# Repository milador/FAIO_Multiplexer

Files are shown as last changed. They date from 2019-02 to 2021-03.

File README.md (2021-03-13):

 # FAIO Multiplexer Switch 

FAIO Multiplexer is an open-source Assistive technology wing for Adafruit Feather boards which enables those with limited or no hand movement to use Adaptive switches as input to operate in multiple input modes.

<p align="center">
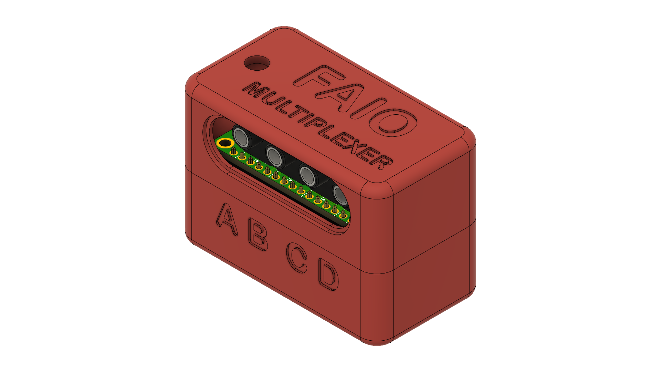
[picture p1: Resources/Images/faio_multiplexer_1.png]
FAIO Multiplexer 1

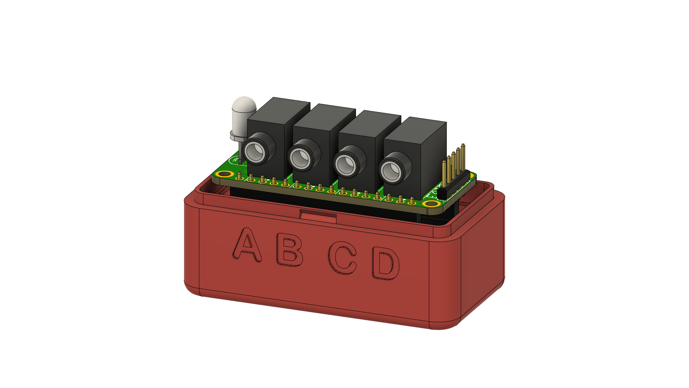
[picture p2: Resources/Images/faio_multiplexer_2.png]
FAIO Multiplexer 2

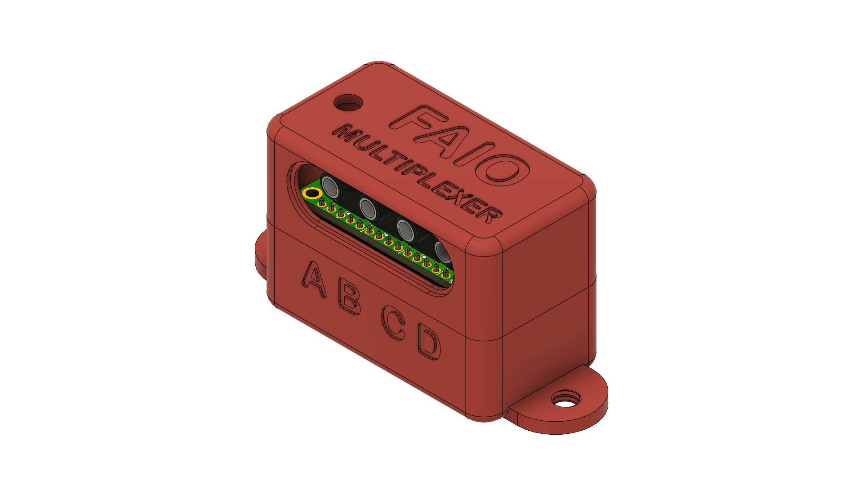
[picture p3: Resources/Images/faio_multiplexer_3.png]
FAIO Multiplexer 3

</p>

FAIO Multiplexer USB supports following switch modes:

* Switch Access Mode ( HID Keyboard ) : Teal Led
* Morse Keyboard Mode ( HID Keyboard ) : Purple Led
* Morse Mouse Mode ( HID Mouse ) : Pink Led
* Settings Mode : Orange Led

FAIO Multiplexer Joystick supports following switch modes:

* Mode 1 (Button 1,Button 2,Button 3,Button 4) : Teal Led
* Mode 2 (Button 5,Button 6,Button 7,Button 8) : Pink Led
* Settings Mode : Orange Led

How to change the mode?

You can change the mode by holding switch number 4 or D for 2 seconds.

Additional firmware to operate Xbox Adaptive Controller using switch module is available as well.

# Downloads 

These are all the files and documentation associated with the FAIO Multiplexer project.

 <table style="width:100%">
  <tr>
    <th>Resource</th>
    <th>Version</th>
    <th>Format</th>
    <th>Link</th>
  </tr>
    <tr>
    <td>FAIO Multiplexer All</td>
    <td>1.1</td>
    <td>ZIP</td>
    <td><a href="https://github.com/milador/FAIO_Multiplexer/archive/master.zip">FAIO_Multiplexer-master.zip</a></td>
  </tr>
  <tr>
    <td>FAIO_Multiplexer Assembly Manual</td>
    <td>Version 1.11</td>
    <td>PDF</td>
    <td><a href="https://github.com/milador/FAIO_Multiplexer/blob/master/Documentation/Build_Manuals/FAIO_Multiplexer_Instructions_Manual.pdf">FAIO_Multiplexer_Instructions_Manual.pdf</a></td>
  </tr>
   <tr>
    <td>FAIO_Multiplexer USB User Manual</td>
    <td>Version 1.1</td>
    <td>PDF</td>
    <td><a href="https://github.com/milador/FAIO_Multiplexer/blob/master/Documentation/User_Manuals/FAIO_Multiplexer_USB_User_Manual.pdf">FAIO_Multiplexer_USB_User_Manual.pdf</a></td>
  </tr>
    <tr>
    <td>FAIO_Multiplexer Joystick User Manual</td>
    <td>Version 1.1</td>
    <td>PDF</td>
    <td><a href="https://github.com/milador/FAIO_Multiplexer/blob/master/Documentation/User_Manuals/FAIO_Multiplexer_Joystick_User_Manual.pdf">FAIO_Multiplexer_Joystick_User_Manual.pdf</a></td>
  </tr>
  <tr>
    <td>FAIO_Multiplexer Switch BOM (csv)</td>
    <td>Jan 11, 2021</td>
    <td>CSV</td>
    <td><a href="https://github.com/milador/FAIO_Multiplexer/blob/master/Components/FAIO_Multiplexer_BOM.csv">FAIO_Multiplexer_BOM.csv</a></td>
  </tr>
  <tr>
    <td>FAIO_Multiplexer Switch BOM (HTML)</td>
    <td>March 12, 2021</td>
    <td>HTML</td>
    <td><a href="http://milador.ca/projects/faio_multiplexer/bom.html">bom.html</a></td>
  </tr>
  <tr>
    <td>FAIO_Multiplexer USB Switch Software</td>
    <td>1.0</td>
    <td>Ino</td>
    <td><a href="https://github.com/milador/FAIO-2/raw/master/Software/FAIO_Multiplexer_USB_Software/FAIO_Multiplexer_USB_Software.ino">FAIO_Multiplexer_USB_Software.ino</a></td>
  </tr>
  <tr>
    <td>FAIO_Multiplexer Joystick Switch Software</td>
    <td>1.0</td>
    <td>Ino</td>
    <td><a href="https://github.com/milador/FAIO-2/raw/master/Software/FAIO_Multiplexer_Joystick_Software/FAIO_Multiplexer_Joystick_Software.ino">FAIO_Multiplexer_Joystick_Software.ino</a></td>
  </tr>
  <tr>
    <td>FAIO_Multiplexer Switch Board Layout</td>
    <td>1.0</td>
    <td>BRD</td>
    <td><a href="https://raw.githubusercontent.com/milador/FAIO_Multiplexer/master/Hardware/PCB_design/FAIO_Multiplexer.brd">FAIO_Multiplexer.brd</a></td>
  </tr>
  <tr>
    <td>FAIO_Multiplexer Switch Board Schematic</td>
    <td>1.0</td>
    <td>SCH</td>
    <td><a href="https://raw.githubusercontent.com/milador/FAIO_Multiplexer/master/Hardware/PCB_design/FAIO_Multiplexer.sch">FAIO_Multiplexer.sch</a></td>
  </tr>
   <tr>
    <td>FAIO_Multiplexer Battery Holder enclosure</td>
    <td>1.1</td>
    <td>STL</td>
    <td><a href="https://github.com/milador/FAIO_Multiplexer/blob/master/Hardware/Housing_design/STL/FAIO_Multiplexer_Body_Battery_Holder.stl">FAIO_Multiplexer_Body_Battery_Holder.stl</a></td>
  </tr>
  <tr>
    <td>FAIO_Multiplexer Bottom enclosure</td>
    <td>1.1</td>
    <td>STL</td>
    <td><a href="https://github.com/milador/FAIO_Multiplexer/blob/master/Hardware/Housing_design/STL/FAIO_Multiplexer_Body_Bottom.stl">FAIO_Multiplexer_Body_Bottom.stl</a></td>
  </tr>
  <tr>
    <td>FAIO_Multiplexer Bottom enclosure with camera mount threaded screw hole</td>
    <td>1.1</td>
    <td>STL</td>
    <td><a href="https://github.com/milador/FAIO_Multiplexer/blob/master/Hardware/Housing_design/STL/FAIO_Multiplexer_Body_Bottom_With_Mount.stl">FAIO_Multiplexer_Body_Bottom_With_Mount.stl</a></td>
  </tr>
  <tr>
    <td>FAIO_Multiplexer Top enclosure</td>
    <td>1.1</td>
    <td>STL</td>
    <td><a href="https://github.com/milador/FAIO_Multiplexer/blob/master/Hardware/Housing_design/STL/FAIO_Multiplexer_Body_Top.stl">FAIO_Multiplexer_Body_Top.stl</a></td>
  </tr>
</table> 

# Usage

The FAIO Multiplexer switch interface can operate in 4 modes and switch D is used to switch between them.The RGB Led blinks 2 times to indicate the current mode.

<p align="center">
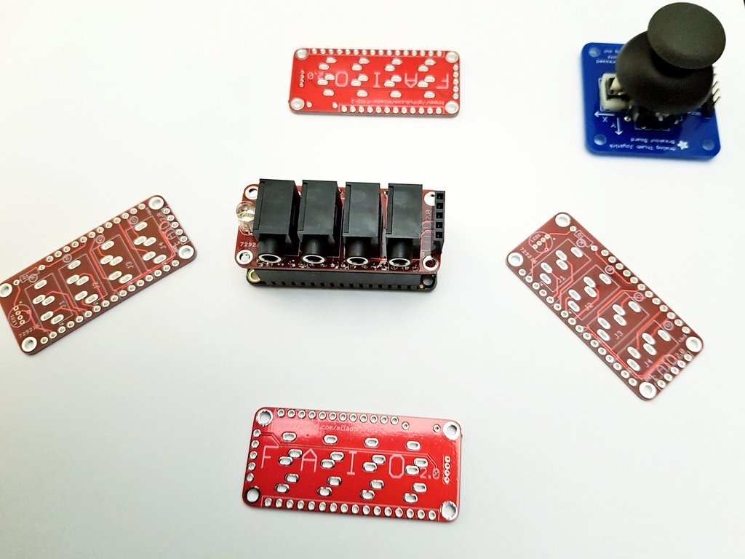
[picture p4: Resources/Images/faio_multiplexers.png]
FAIO Multiplexer boards

</p>

## USB or Bluetooth Switch mode

 <table style="width:100%">
  <tr>
    <th>Mode Number</th>
    <th>Mode</th>
    <th>Color</th>
  </tr>
    <tr>
    <td>1</td>
    <td>Keyboard Switch</td>
    <td>Teal</td>
  </tr>
  <tr>
    <td>2</td>
    <td>Morse Keyboard</td>
    <td>Purple</td>
  </tr>
  <tr>
    <td>3</td>
    <td>Morse Mouse</td>
    <td>Pink</td>
  </tr>
  <tr>
    <td>4</td>
    <td>Settings</td>
    <td>Orange</td>
  </tr>
</table> 

<p align="center">
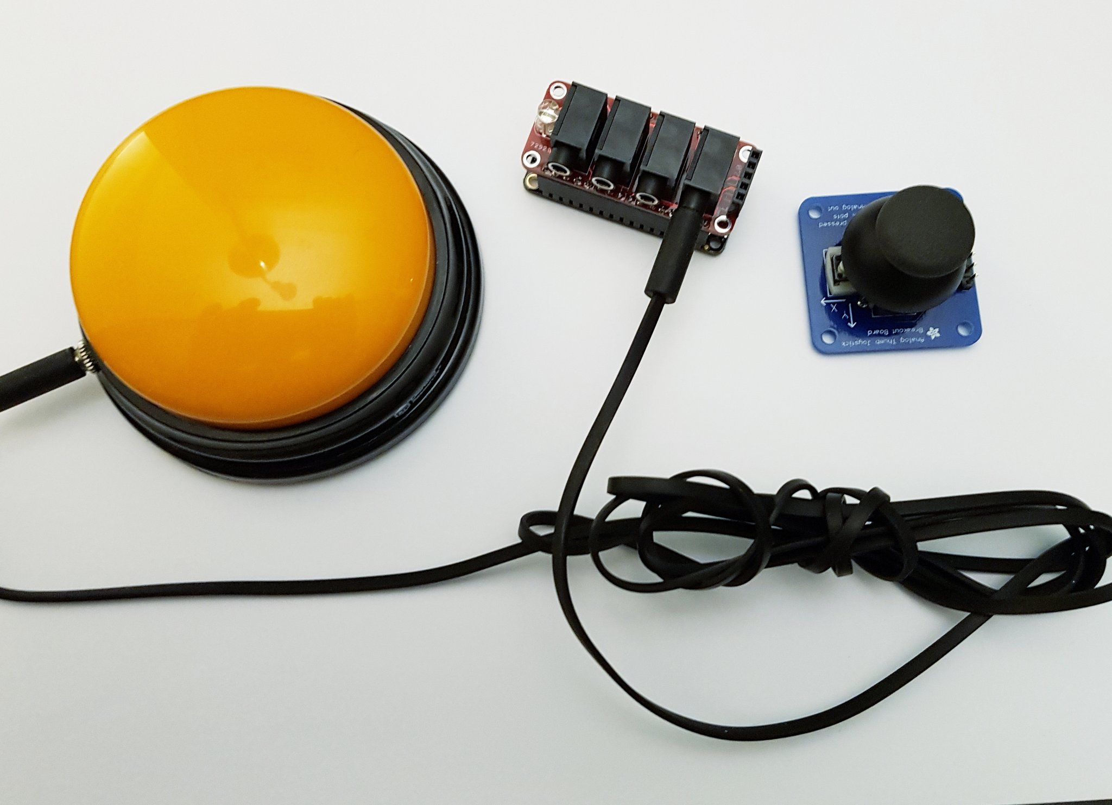
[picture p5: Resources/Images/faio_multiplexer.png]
FAIO Multiplexer board

</p>

## Joystick Switch mode

 <table style="width:100%">
  <tr>
    <th>Joystick Button Number (Mode 1,Mode 2)</th>
    <th>Xbox Button</th>
    <th>Color</th>
  </tr>
    <tr>
    <td>(1,5)</td>
    <td>X1</td>
    <td>Blue</td>
  </tr>
  <tr>
    <td>(2,6)</td>
    <td>X2</td>
    <td>Yellow</td>
  </tr>
  <tr>
    <td>(3,7)</td>
    <td>A</td>
    <td>Green</td>
  </tr>
  <tr>
    <td>(4,8)</td>
    <td>B</td>
    <td>Red</td>
  </tr>
</table> 

## Software Setup Instructions

  1. Install the required libraries 
  
  1.1. Install Neo Pixels : https://github.com/adafruit/Adafruit_NeoPixel

  1.2. Install EasyMorse if using USB or Bluetooth version : https://github.com/milador/EasyMorse
  
  1.3. Install StopWatch if using USB or Bluetooth version : https://github.com/RobTillaart/Arduino/tree/master/libraries/StopWatch
  
  1.4. Install FlashStorage if using Feather M0 Board : https://github.com/cmaglie/FlashStorage

  1.5. Install Joystick library: https://github.com/MHeironimus/ArduinoJoystickLibrary or https://github.com/gdsports/ArduinoJoystickLibrary/tree/samd_patch
  
  2. Download the firmware 
  
  2.1. USB Firmware : https://github.com/milador/FAIO_Multiplexer/raw/master/Software/FAIO_Multiplexer_USB_Software/FAIO_Multiplexer_USB_Software.ino

  2.2. Joystick Firmware : https://github.com/milador/FAIO_Multiplexer/raw/master/Software/FAIO_Multiplexer_Joystick_Software/FAIO_Multiplexer_Joystick_Software.ino
  
  2.3. Bluetooth Firmware (Coming up)
  
  3. Setup Arduino IDE for your feather board according to the instructions on Adafruit website
  
  4. Verify and upload firmware code to your Feather Board

# License

## Creative Commons Attribution-NonCommercial-ShareAlike (CC-BY-NC-SA)

Copyright (c) 2018 Milador

A creative commons license that bans commercial use and requires you to release any modified works under this license.

<p align="center">
CC-BY-NC-SA
</p>

<br />This work is licensed under a <a rel="license" href="http://creativecommons.org/licenses/by-nc-sa/3.0/">Creative Commons Attribution-NonCommercial-ShareAlike 3.0 Unported License</a>.

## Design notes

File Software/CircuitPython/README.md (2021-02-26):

# FAIO-Multiplexer CircuitPython software setup

  1. Download latest version of [CircuitPython for Feather M0 Express UF2](https://circuitpython.org/board/feather_m0_express/)
  2. Plug your Feather M0 Express into your computer using a known-good USB cable
  3. Double-click the small RST (reset) button, and you will see the NeoPixel RGB LED turn green
  4. You will see a new disk drive appear called FEATHERBOOT under Device and Drivers 
  5. Drag the adafruit_circuitpython_etc.uf2 file to FEATHERBOOT
  6. The red LED will flash. Then, the FEATHERBOOT drive will disappear and a new disk drive called CIRCUITPY will appear
  7. Replace the code.py under CIRCUITPY drive with FAIO Multiplexer USB [code.py](https://raw.githubusercontent.com/milador/FAIO_Multiplexer/main/Software/CircuitPython/FAIO_Multiplexer_USB_Software/code.py)
  8. Drag and drop required libraries under CIRCUITPY drive in lib folder. [Required libraries](https://github.com/milador/FAIO_Multiplexer/tree/main/Software/CircuitPython/FAIO_Multiplexer_USB_Software/lib)
  9. The led on Enabled-Controller-Mini should turn to teal color

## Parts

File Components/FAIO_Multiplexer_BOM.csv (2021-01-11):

Index | Quantity | Digikey Part Number | Manufacturer Part Number | Description | Unit Price (US) | Total Price (US) | Link
1 | 1 | 1528-1514-ND | 2771 | FEATHER 32U4 BASIC PROTO | 19.95 |  | https://www.digikey.com/product-detail/en/adafruit-industries-llc/2771/1528-1514-ND/
2 | 1 | 1568-1213-ND | COM-12986 | ADDRESS LED DISC SER RGB 5MM 5PC | 2.95 |  | https://www.digikey.com/products/en?keywords=COM-12986
3 | 1 | 1528-1560-ND | 2886 | FEATHER HEADER KIT FML | 0.95 |  | https://www.digikey.com/product-detail/en/adafruit-industries-llc/2886/1528-1560-ND/
4 | 1 | CF14JT470RCT-ND | CF14JT470R | RES 470 OHM 1/4W 5% AXIAL | 0.1 |  | https://www.digikey.com/product-detail/en/stackpole-electronics-inc/CF14JT470R/CF14JT470RCT-ND/1830342
5 | 4 | CP1-3535NG-ND | SJ1-3535NG | CONN JACK STEREO 3.5MM R/A | 1.25 |  | https://www.digikey.com/product-detail/en/cui-inc/SJ1-3535NG/CP1-3535NG-ND
6 | 4 | 36-4687-ND | 4687 | HEX NUT 0.197" NYLON M2.5 | 0.15 |  | https://www.digikey.com/en/products/detail/keystone-electronics/4687/4499296
7 | 4 | 36-29334-ND | 29334 | MACH SCREW PAN SLOTTED M2.5X0.45 | 0.22 |  | https://www.digikey.com/en/products/detail/keystone-electronics/29334/1532988
8 | 1 | 732-5318-ND | 61300511121 | CONN HEADER VERT 5POS 2.54MM | 0.25 |  | https://www.digikey.com/product-detail/en/wurth-electronics-inc/61300511121/732-5318-ND
9 | 1 | 1528-1858-ND | 2750 | BATTERY LITHIUM 3.7V 350MAH (Optional) | 6.95 |  | https://www.digikey.com/en/products/detail/adafruit-industries-llc/2750/6612470
 |  |  |  |  | Subtotal | 30.68

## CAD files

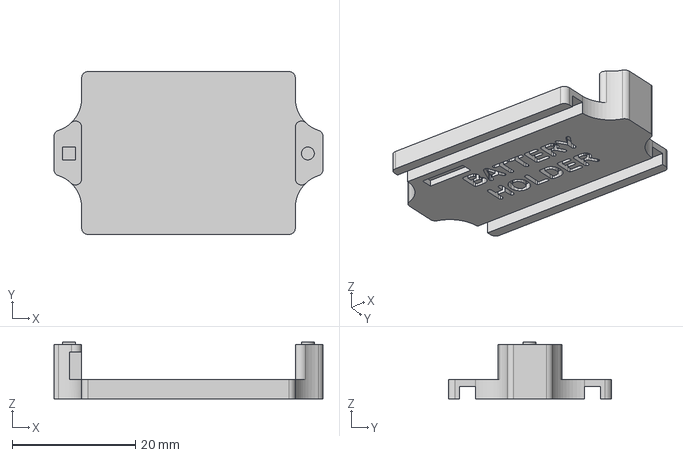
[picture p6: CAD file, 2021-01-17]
Hardware/Housing_design/STEP/FAIO_Multiplexer_Body_Battery_Holder.step
43.7 x 26.5 x 9.20 mm

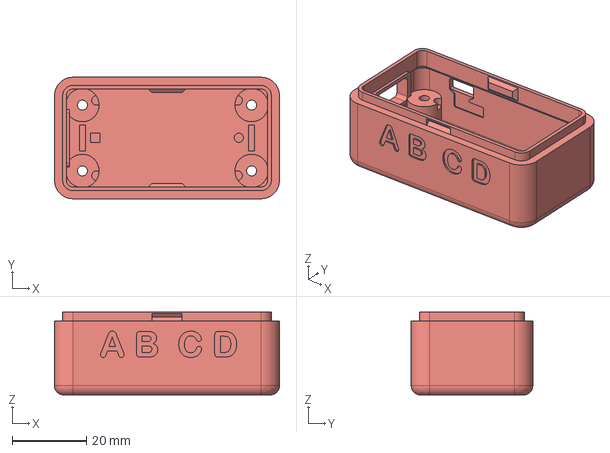
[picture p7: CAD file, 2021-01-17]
Hardware/Housing_design/STEP/FAIO_Multiplexer_Body_Bottom.step
60.8 x 32.9 x 22.4 mm

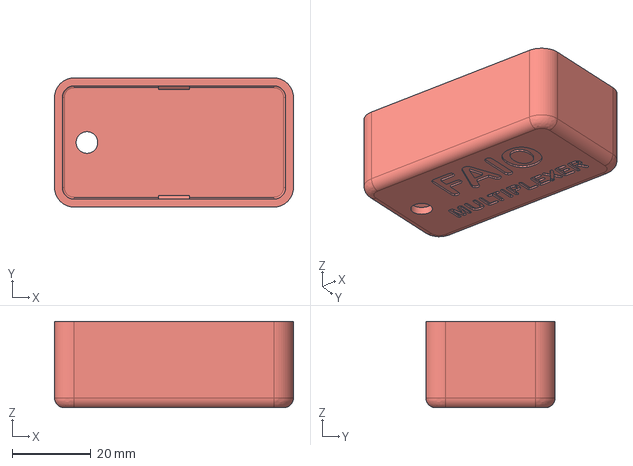
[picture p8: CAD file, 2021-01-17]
Hardware/Housing_design/STEP/FAIO_Multiplexer_Body_Top.step
60.8 x 32.9 x 22.0 mm

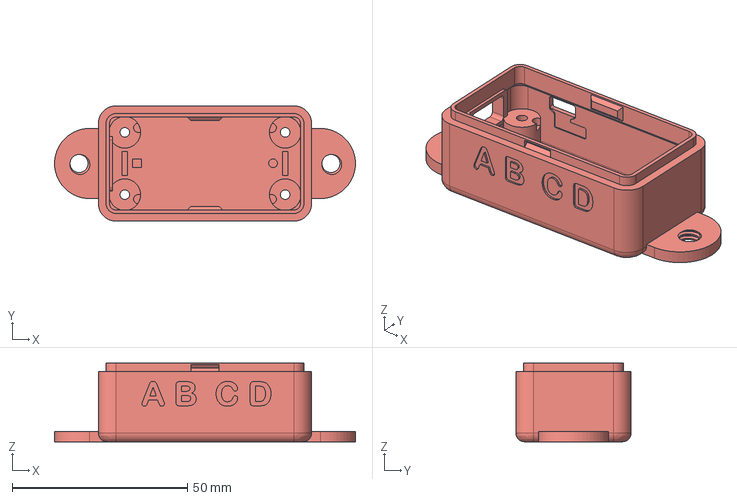
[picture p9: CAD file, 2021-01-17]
Hardware/Housing_design/STEP/FAIO_Multiplexer_Body_Bottom_With_Mount.step
85.8 x 32.9 x 22.4 mm

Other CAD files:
Hardware/Housing_design/STL/FAIO_Multiplexer_Body_Battery_Holder.stl
Hardware/Housing_design/STL/FAIO_Multiplexer_Body_Bottom.stl
Hardware/Housing_design/STL/FAIO_Multiplexer_Body_Bottom_With_Mount.stl
Hardware/Housing_design/STL/FAIO_Multiplexer_Body_Top.stl

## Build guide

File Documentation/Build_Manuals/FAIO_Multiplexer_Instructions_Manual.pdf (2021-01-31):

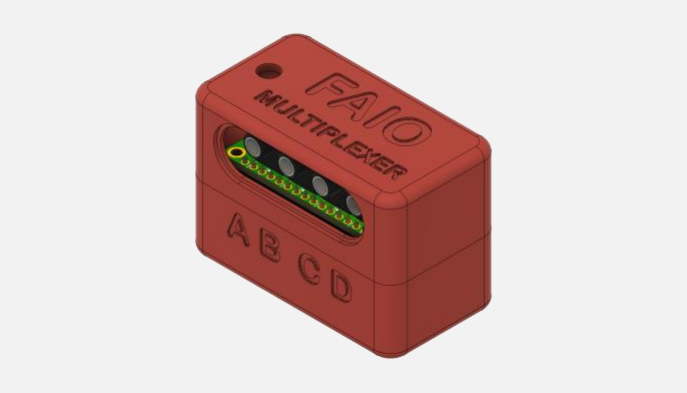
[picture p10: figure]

# FAIO MULTIPLEXER INSTRUCTIONS MANUAL (V1.11)

What if you could have a switch interface that would let you perform many actions using only 4 switches?

### Milad Hajihassan

https://github.com/milador/FAIO_Multiplexer

1

## Contents

Components List | 2
Software | 3
Installing Arduino Libraries | 3
USB Version | 3
Board Support Packages | 3
Required Software and libraries | 3
Uploading Software | 5
XAC Joystick Version | 6
Board Support Packages | 6
Required Software and libraries | 6
Uploading Software | 7
Wireless Version | 8
Board Support Packages | 8
Required Software and libraries | 8
Uploading Software | 10
Hardware Assembly | 11
Printed circuit Board design | 11
Enclosure design | 11
Assembly Instructions | 12

2

## Components List

1. ADAFRUIT FEATHER x 1
A. USB Version: ADAFRUIT FEATHER 32U4 BASIC PROTO or ADAFRUIT FEATHER M0 BASIC

PROTO

B. XAC Joystick Version: ADAFRUIT FEATHER 32U4 BASIC PROTO
C. Wireless Version: ADAFRUIT FEATHER 32U4 Bluefruit LE or ADAFRUIT FEATHER M0

Bluefruit LE

2. ADDRESS LED DISC SER RGB 5MM x 1
3. FEATHER HEADER KIT FML x 1
4. RES 470 OHM 1/4W 5% AXIAL x 1
5. CONN JACK STEREO 3.5MM R/A x 4
6. HEX NUT 0.197" NYLON M2.5 x 4
7. MACH SCREW PAN SLOTTED M2.5X0.45 x 4
8. CONN HEADER VERT 5POS 2.54MM (Optional: XAC Joystick version) x 1
9. BATTERY LITHIUM 3.7V 350MAH (Optional) x 1

The FAIO_Multiplexer_BOM or FAIO_Multiplexer bill of materials can also be downloaded from

GitHub repository under main directory.

https://github.com/milador/FAIO_Multiplexer/blob/master/Components/FAIO_Multiplexer_BOM.xlsx

3

## Software

The FAIO-Multiplexer software can be downloaded from the GitHub repository under software directory.

The FAIO_Multiplexer hardware can be used along different software as input device for multiple devices. The FAIO_Multiplexer software is offered in the following flavors:

1. USB Version: FAIO_Multiplexer_USB_Software (https://github.com/milador/FAIO_Multiplexer/tree/master/Software/FAIO_Multiplexer_USB_Software)
2. XAC Joystick Version: FAIO_Multiplexer_Joystick_Software (https://github.com/milador/FAIO_Multiplexer/tree/master/Software/FAIO_Multiplexer_Joystick_Software)
3. Wireless Version: FAIO_Multiplexer_Wireless_Software (https://github.com/milador/FAIO_Multiplexer_Wireless/tree/master/Software/FAIO_Multiplexer_Wireless_Software)

### Installing Arduino Libraries

The following instructions on how to install additional Arduino libraries helps you to get started with setting up Arduino IDE with required libraries and dependencies.

https://www.arduino.cc/en/guide/libraries

### USB Version

Board Support Packages
You can find the official instructions to install Board Support Packages on Adafruit website using following link:

https://learn.adafruit.com/adafruit-feather-m0-basic-proto/setup

https://learn.adafruit.com/adafruit-feather-32u4-basic-proto/arduino-ide-setup

Note: Please follow the instructions depending on your Adafruit Feather board model.

Alternatively, you can perform following instructions to install Board Support Packages:

1. Open and start the Arduino IDE.
2. Go to File > Preferences.

### 3. Add following link as a new line under Additional Board Manager URLs

- https://www.adafruit.com/package_adafruit_index.json

### 4. Restart the Arduino IDE 5. Open the Boards Manager option from the Tools > Board menu and install Adafruit SAMD

Boards by Adafruit or Adafruit SAMD Boards by Adafruit depending on your board.
6. Wait until the IDE finishes installing the cross-compiling toolchain and tools associated with Board Support Package. This may take few minutes.
7. That’s it! The installation of Board Support Packages is finished.

Required Software and libraries
The USB version of the software requires the following files and libraries:
- StopWatch library (https://github.com/RobTillaart/Stopwatch_RT)
- EasyMorse library (https://github.com/milador/EasyMorse)
- Adafruit_NeoPixel library (https://github.com/adafruit/Adafruit_NeoPixel)
- FlashStorage library (https://github.com/cmaglie/FlashStorage) (Optional: Only Feather M0 Board)

4

- FAIO_Multiplexer_USB_Software.ino (https://github.com/milador/FAIO_Multiplexer/blob/master/Software/FAIO_Multiplexer_USB_Software/FAIO_Multiplexer_USB_Software.ino)

StopWatch library helps to calculate the reaction time and timeout in the morse code interface.

EasyMorse library is used to provide morse code input interface by translating morse code into characters.

FAIO_Multiplexer is using Adafruit_NeoPixel library to provide visual feedback using RGB LED.

The Feather M0 Board does not come with EEPROM support and requires using FlashStorage library to handle saving variables and settings.

You can use the following instructions to download and install the required libraries:

1. Visit the StopWatch library (https://github.com/RobTillaart/Stopwatch_RT) github repository page.
2. Click on Code > Download Zip to download StopWatch library.

### 3. Extract Stopwatch_RT-master.zip file 4. Rename Stopwatch_RT-master folder to Stopwatch folder under Stopwatch_RT-master

subdirectory.
5. Copy or move Stopwatch folder to Arduino installation library subdirectory. As an example: This is found under C:\Program Files (x86)\Arduino\libraries in windows 10.
6. Visit the EasyMorse library (https://github.com/milador/EasyMorse) github repository page.
7. Click on Code > Download Zip to download EasyMorse library.

### 8. Extract EasyMorse.zip file

9. Rename EasyMorse-master folder to EasyMorse folder under EasyMorse-master subdirectory.
10. Copy or move EasyMorse folder to Arduino installation library subdirectory. As an example: This is found under C:\Program Files (x86)\Arduino\libraries in windows 10.
11. Visit the FlashStorage library (https://github.com/cmaglie/FlashStorage) github repository page.
12. Click on Code > Download Zip to download FlashStorage library.

### 13. Extract FlashStorage.zip file 14. Rename FlashStorage-master folder to FlashStorage folder under FlashStorage -master

subdirectory.
15. Copy or move FlashStorage folder to Arduino installation library subdirectory. As an example: This is found under C:\Program Files (x86)\Arduino\libraries in windows 10.
16. Visit the FAIO_Multiplexer_USB_Software.ino (https://github.com/milador/FAIO_Multiplexer/blob/master/Software/FAIO_Multiplexer_USB_Software/FAIO_Multiplexer_USB_Software.ino) raw source code file under FAIO_Multiplexer github repository page.

### 17. Right click on the source code or any place on this page and select Save Page As…

18. Select the directory you would like to save the software in your computer.
19. Change File name from FAIO_Multiplexer_USB_Software to FAIO_Multiplexer_USB_Software.ino
20. Change Save as type to All Files.
21. Click on Save button.
22. Open the directory you selected in step 18.

### 23. Double left click or open FAIO_Multiplexer_USB_Software file

5

### 24. Arduino IDE will ask your permission to create a new sketch folder named

FAIO_Multiplexer_USB_Software and move FAIO_Multiplexer_USB_Software.ino under this folder.
25. Click on the Ok button.
26. Arduino IDE should now open the FAIO_Multiplexer_USB_Software.ino file automatically.

Uploading Software
Note: Make sure all three files are included in your local copy of Software directory before uploading it to the Adafruit Feather board. The libraries can be installed in Arduino libraries.

You can go ahead and upload the downloaded. ino software to Adafruit Feather board using Arduino IDE once all the necessary libraries are installed.

1. Select the Board under Tools > Board > Adafruit Boards as Adafruit Feather 32u4 or under Tools > Board > Adafruit SAMD Boards as Adafruit Feather M0 based on your board.
2. Select the correct port number under Tools > Port which should say COM XX (Adafruit Feather 32u4) or COM XX (Adafruit Feather M0) based on your board

Note: It’s very important to make sure the correct Board and port number are selected as selecting the wrong board may result problems with bootloader of Adafruit Feather board.

3. Press the Verify button to make sure there is no problem with the software and libraries.
4. Press Upload button

Here you can see an example of my selected Board and port number.

Note: Your port number will not be the same

You can now go ahead and upload the software. Arduino IDE will show you a Done uploading message indicating the software is uploaded to your FAIO_Multiplexer.

The LED on the FAIO_Multiplexer main board blinks two times in green to indicate the start of initialization process has been started and it will blink again two times in green to indicate end of the initialization process.

You can also open the Serial Monitor in Arduino IDE on 115200 baud rate to read initialization information about the version of software.

6

### XAC Joystick Version

Board Support Packages
You can find the official instructions to install Board Support Packages on Adafruit website using following link:

https://learn.adafruit.com/adafruit-feather-32u4-basic-proto/arduino-ide-setup

Alternatively, you can perform following instructions to install Board Support Packages:

1. Open and start the Arduino IDE.
2. Go to File > Preferences.

### 3. Add following link as a new line under Additional Board Manager URLs

- https://www.adafruit.com/package_adafruit_index.json

### 4. Restart the Arduino IDE

5. Open the Boards Manager option from the Tools > Board menu and install Adafruit AVR Boards by Adafruit
6. Wait until the IDE finishes installing the cross-compiling toolchain and tools associated with Board Support Package. This may take few minutes.
7. That’s it! The installation of Board Support Packages is finished.

Required Software and libraries
The XAC Joystick version of the software requires the following files and libraries:
- StopWatch library (https://github.com/RobTillaart/Stopwatch_RT)
- Joystick library (https://github.com/MHeironimus/ArduinoJoystickLibrary)
- Adafruit_NeoPixel library (https://github.com/adafruit/Adafruit_NeoPixel)
- FAIO_Multiplexer_Joystick_Software.ino (https://github.com/milador/FAIO_Multiplexer/blob/master/Software/FAIO_Multiplexer_Joystick_Software/FAIO_Multiplexer_Joystick_Software.ino)

The joystick library is used to turn FAIO_Multiplexer into a joystick USB HID device which can be supported by Xbox adaptive controller.

FAIO_Multiplexer is using Adafruit_NeoPixel library to provide visual feedback using RGB LED.

You can use the following instructions to download and install the required libraries:

1. Visit the StopWatch library (https://github.com/RobTillaart/Stopwatch_RT) github repository page.
2. Click on Code > Download Zip to download StopWatch library.

### 3. Extract Stopwatch_RT-master.zip file 4. Rename Stopwatch_RT-master folder to Stopwatch folder under Stopwatch_RT-master

subdirectory.
5. Copy or move Stopwatch folder to Arduino installation library subdirectory. As an example: This is found under C:\Program Files (x86)\Arduino\libraries in windows 10.
6. Visit the Joystick library (https://github.com/MHeironimus/ArduinoJoystickLibrary) github repository page.

7

7. Click on Code > Download Zip to download ArduinoJoystickLibrary library.

### 8. Extract ArduinoJoystickLibrary.zip file

9. Copy or move Joystick folder under ArduinoJoystickLibrary-master subdirectory to Arduino installation library subdirectory. As an example: This is found under C:\Program Files (x86)\Arduino\libraries in windows 10.
10. Visit the FAIO_Multiplexer_Joystick_Software.ino (https://github.com/milador/FAIO_Multiplexer/blob/master/Software/FAIO_Multiplexer_Joystick_Software/FAIO_Multiplexer_Joystick_Software.ino) raw source code file under FAIO_Multiplexer github repository page.

### 11. Right click on the source code or any place on this page and select Save Page As…

12. Select the directory you would like to save the software in your computer.

### 13. Change File name from FAIO_Multiplexer_Joystick_Software to

FAIO_Multiplexer_Joystick_Software.ino
14. Change Save as type to All Files.
15. Click on Save button.
16. Open the directory you selected in step 12.

### 17. Double left click or open FAIO_Multiplexer_Joystick_Software file 18. Arduino IDE will ask your permission to create a new sketch folder named

FAIO_Multiplexer_Joystick_Software and move FAIO_Multiplexer_Joystick_Software.ino under this folder.
19. Click on the Ok button.
20. Arduino IDE should now open the FAIO_Multiplexer_Joystick_Software.ino file automatically.

Uploading Software
Note: Make sure all three files are included in your local copy of Software directory before uploading it to the Adafruit Feather board. The libraries can be installed in Arduino libraries.

You can go ahead and upload the downloaded. ino software to Adafruit Feather board using Arduino IDE once all the necessary libraries are installed.

### 1. Select the Board under Tools > Board > Adafruit Boards as Adafruit Feather 32u4

2. Select the correct port number under Tools > Port which should say COM XX (Adafruit Feather 32u4)

Note: It’s very important to make sure the correct Board and port number are selected as selecting the wrong board may result problems with bootloader of Adafruit Feather board.

3. Press the Verify button to make sure there is no problem with the software and libraries.

### 4. Press Upload button

Here you can see an example of my selected Board and port number.

Note: Your port number will not be the same

You can now go ahead and upload the software. Arduino IDE will show you a Done uploading message indicating the software is uploaded to your FAIO_Multiplexer.

8

The LED on the FAIO_Multiplexer main board blinks two times in green to indicate the start of initialization process has been started and it will blink again two times in green to indicate end of the initialization process.

You can also open the Serial Monitor in Arduino IDE on 115200 baud rate to read initialization information about the version of software.

### Wireless Version

Board Support Packages
You can find the official instructions to install Board Support Packages on Adafruit website using following links:

https://learn.adafruit.com/adafruit-feather-m0-bluefruit-le/setup

https://learn.adafruit.com/adafruit-feather-32u4-bluefruit-le//setup

Note: Please follow the instructions depending on your Adafruit Feather board model.

The wireless version of the FAIO_Multiplexer is using nRF51 Bluetooth chip to communicate with host devices. Bluetooth communication might seem complicated but Adafruit has made the bluetooth communication process less challenging by providing Adafruit nRF51 BLE Library which you can download from Adafruit and import it to your locally installed Arduino directory under libraries directory.

https://github.com/adafruit/Adafruit_BluefruitLE_nRF51

The instructions on how to install Adafruit nRF51 BLE Library can be found in following link:

https://learn.adafruit.com/adafruit-feather-32u4-bluefruit-le/installing-ble-library

Alternatively, you can perform following instructions to install Board Support Packages:

1. Open and start the Arduino IDE.
2. Go to File > Preferences.

### 3. Add following link as a new line under Additional Board Manager URLs

- https://www.adafruit.com/package_adafruit_index.json

### 4. Restart the Arduino IDE 5. Open the Boards Manager option from the Tools > Board menu and install Adafruit SAMD

Boards by Adafruit or Adafruit SAMD Boards by Adafruit depending on your board.
6. Wait until the IDE finishes installing the cross-compiling toolchain and tools associated with Board Support Package. This may take few minutes.
7. That’s it! The installation of Board Support Packages is finished.

Required Software and libraries
The wireless version of the software requires the following files and libraries:
- StopWatch library (https://github.com/RobTillaart/Stopwatch_RT)
- EasyMorseBlue library (https://github.com/milador/EasyMorseBlue)
- Adafruit_NeoPixel library (https://github.com/adafruit/Adafruit_NeoPixel)

9

- FlashStorage library (https://github.com/cmaglie/FlashStorage) (Optional: Only Feather M0 Board)
- Bluefruit Arduino Library (https://learn.adafruit.com/adafruit-feather-32u4-bluefruit-le/installing-ble-library)
- FAIO_Multiplexer_Wireless_Software.ino (https://github.com/milador/FAIO_Multiplexer_Wireless/blob/master/Software/FAIO_Multiplexer_Wireless_Software/FAIO_Multiplexer_Wireless_Software.inoare.ino)

StopWatch library helps to calculate the reaction time and timeout in the morse code interface.

The EasyMorseBlue library is the Bluetooth version of EasyMorse library which is used to enable the end user to use morse code or a sequence of dots and dashes as input method.

FAIO_Multiplexer is using Adafruit_NeoPixel library to provide visual feedback using RGB LED.

1. Visit the StopWatch library (https://github.com/RobTillaart/Stopwatch_RT) github repository page.
2. Click on Code > Download Zip to download StopWatch library.

### 3. Extract Stopwatch_RT-master.zip file 4. Rename Stopwatch_RT-master folder to Stopwatch folder under Stopwatch_RT-master

subdirectory.
5. Copy or move Stopwatch folder to Arduino installation library subdirectory. As an example: This is found under C:\Program Files (x86)\Arduino\libraries in windows 10.
6. Visit the EasyMorseBlue library (https://github.com/milador/EasyMorseBlue) github repository page.
7. Click on Code > Download Zip to download EasyMorseBlue library.

### 8. Extract EasyMorse.zip file 9. Rename EasyMorseBlue-master folder to EasyMorseBlue folder under EasyMorseBlue-master

subdirectory.
10. Copy or move EasyMorseBlue folder to Arduino installation library subdirectory. As an example: This is found under C:\Program Files (x86)\Arduino\libraries in windows 10.
11. Visit the FlashStorage library (https://github.com/cmaglie/FlashStorage) github repository page.
12. Click on Code > Download Zip to download FlashStorage library.

### 13. Extract FlashStorage.zip file 14. Rename FlashStorage-master folder to FlashStorage folder under FlashStorage -master

subdirectory.
15. Copy or move FlashStorage folder to Arduino installation library subdirectory. As an example: This is found under C:\Program Files (x86)\Arduino\libraries in windows 10.

### 16. Click on Sketch > Include Library > Manage Libraries…

17. Search for the Adafruit BluefruitLE nRF51 library and install it.
18. Visit the FAIO_Multiplexer_Wireless_Software.ino (https://github.com/milador/FAIO_Multiplexer_Wireless/blob/master/Software/FAIO_Multiplexer_Wireless_Software/FAIO_Multiplexer_Wireless_Software.inoare.ino) raw source code file under FAIO-Multiplexer github repository page.

### 19. Right click on the source code or any place on this page and select Save Page As…

20. Select the directory you would like to save the software in your computer.

### 21. Change File name from FAIO_Multiplexer_Wireless_Software to

FAIO_Multiplexer_Wireless_Software.ino
22. Change Save as type to All Files.
23. Click on Save button.
24. Open the directory you selected in step 20.

### 25. Double left click or open FAIO_Multiplexer_Wireless_Software file

10

### 26. Arduino IDE will ask your permission to create a new sketch folder named

FAIO_Multiplexer_Wireless_Software and move FAIO_Multiplexer_Wireless_Software.ino under this folder.
27. Click on the Ok button.
28. Arduino IDE should now open the FAIO_Multiplexer_Wireless_Software.ino file automatically.

Uploading Software
Note: Make sure all three files are included in your local copy of Software directory before uploading it to the Adafruit Feather board. The libraries can be installed in Arduino libraries.

You can go ahead and upload the downloaded. ino software to Adafruit Feather board using Arduino IDE once all the necessary libraries are installed.

1. Select the Board under Tools > Board > Adafruit Boards as Adafruit Feather 32u4 or under Tools > Board > Adafruit SAMD Boards as Adafruit Feather M0 based on your board.
2. Select the correct port number under Tools > Port which should say COM XX (Adafruit Feather 32u4) or COM XX (Adafruit Feather M0) based on your board

Note: It’s very important to make sure the correct Board and port number are selected as selecting the wrong board may result problems with bootloader of Adafruit Feather board.

1. Press the Verify button to make sure there is no problem with the software and libraries.

### 2. Press Upload button

You can now go ahead and upload the software. Arduino IDE will show you a Done Uploading message indicating the software is uploaded to your FAIO_Multiplexer.

The LED on the FAIO_Multiplexer main board blinks two times in teal to indicate the start of initialization process has been started and it will blink again two times in green to indicate end of the initialization process.

You can also open the Serial Monitor in Arduino IDE on 115200 baud-rate to read initialization information about the version of software.

11

## Hardware Assembly

### Printed circuit Board design

The printed circuit boards (PCB) can be downloaded from GitHub repository under Hardware directory.

https://github.com/milador/FAIO_Multiplexer/tree/master/Hardware/PCB_design

### Enclosure design

The enclosure/housing files in STL format can be downloaded from GitHub repository under Hardware directory.

https://github.com/milador/FAIO_Multiplexer/tree/master/Hardware/Housing_design

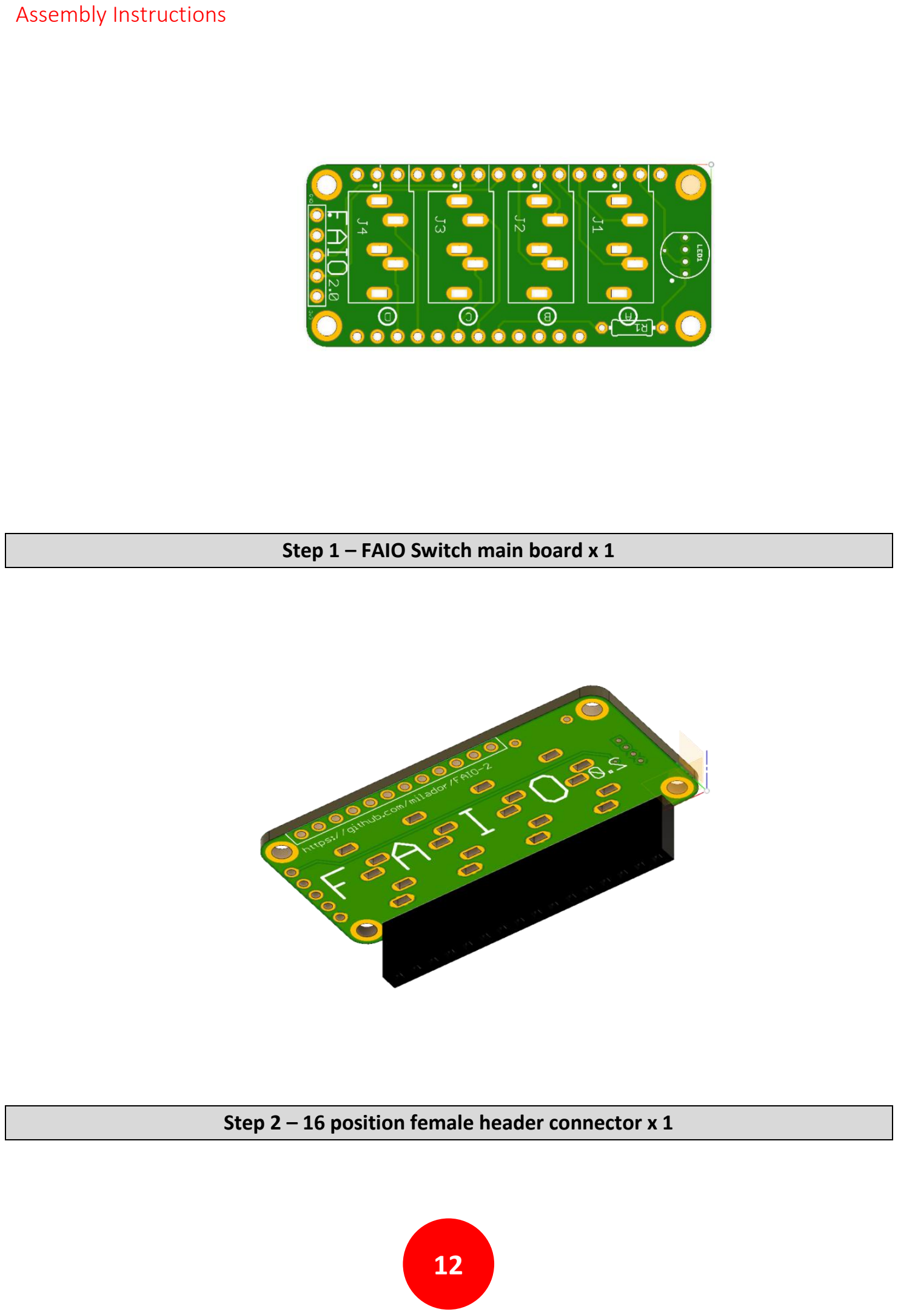
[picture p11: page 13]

12

### Assembly Instructions

Step 1 – FAIO Switch main board x 1
Step 2 – 16 position female header connector x 1

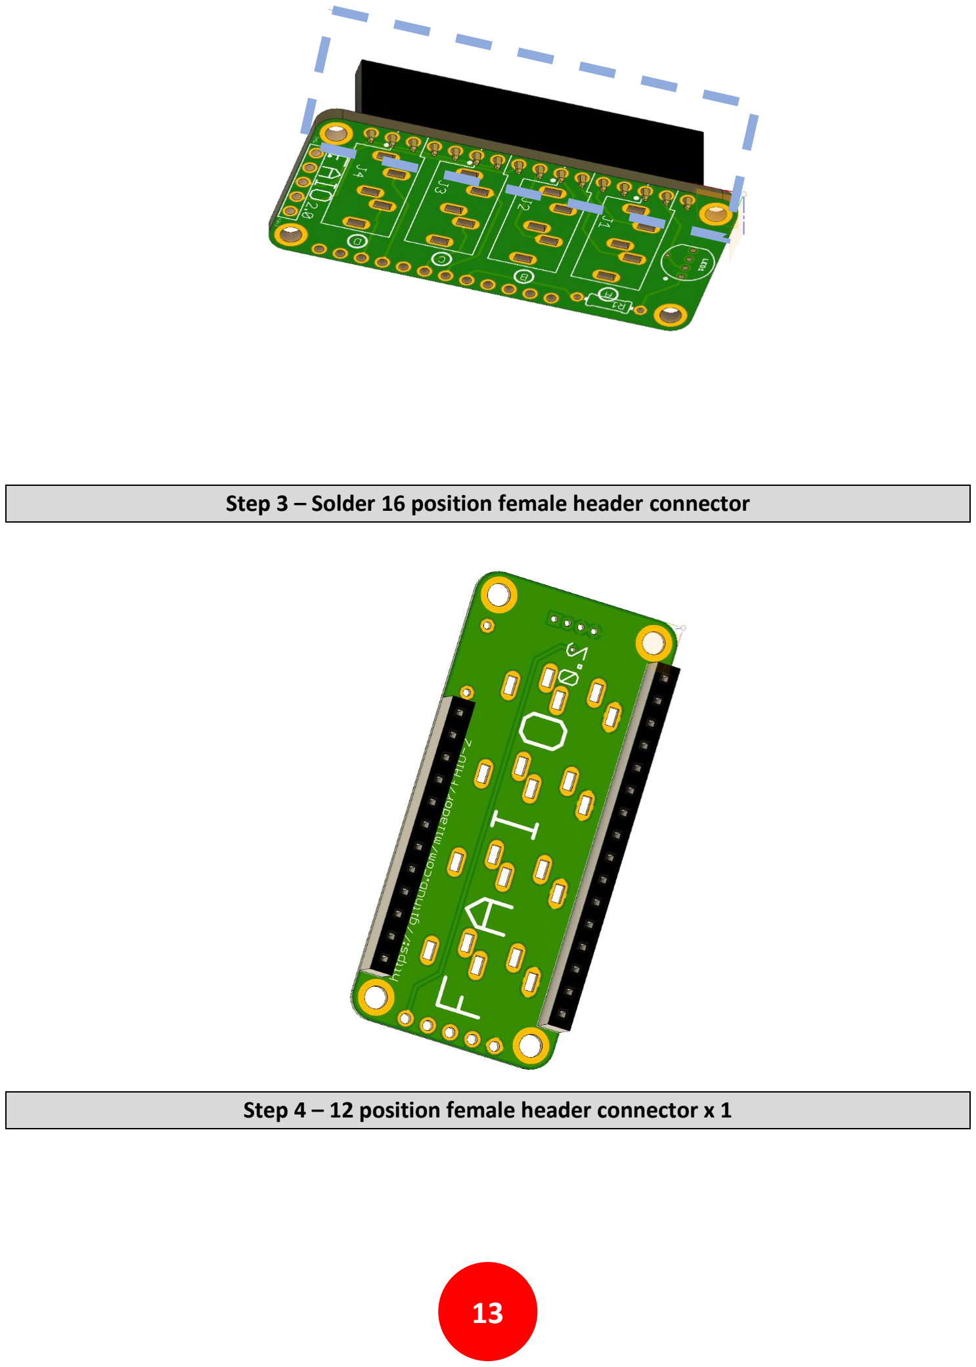
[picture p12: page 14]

13

Step 3 – Solder 16 position female header connector
Step 4 – 12 position female header connector x 1

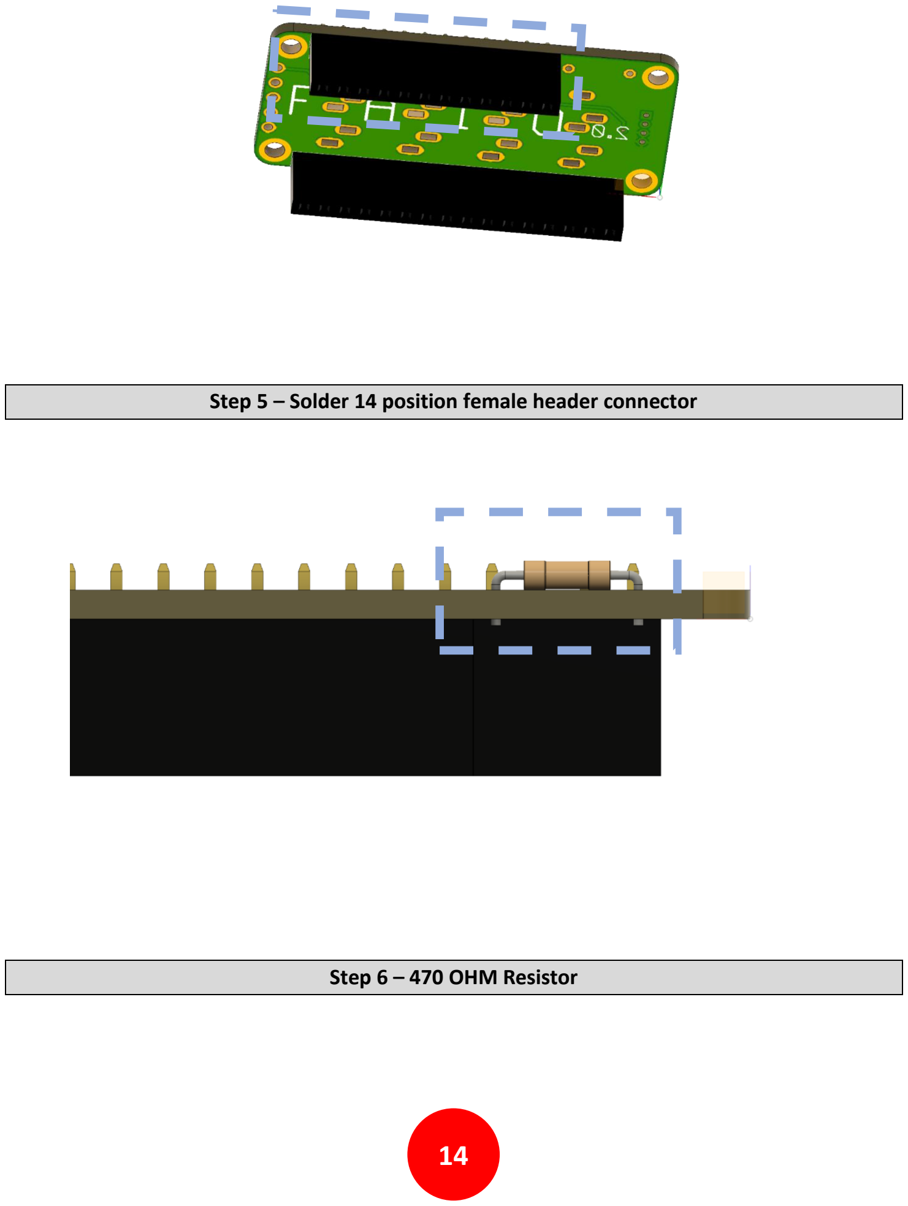
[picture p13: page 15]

14

Step 5 – Solder 14 position female header connector
Step 6 – 470 OHM Resistor

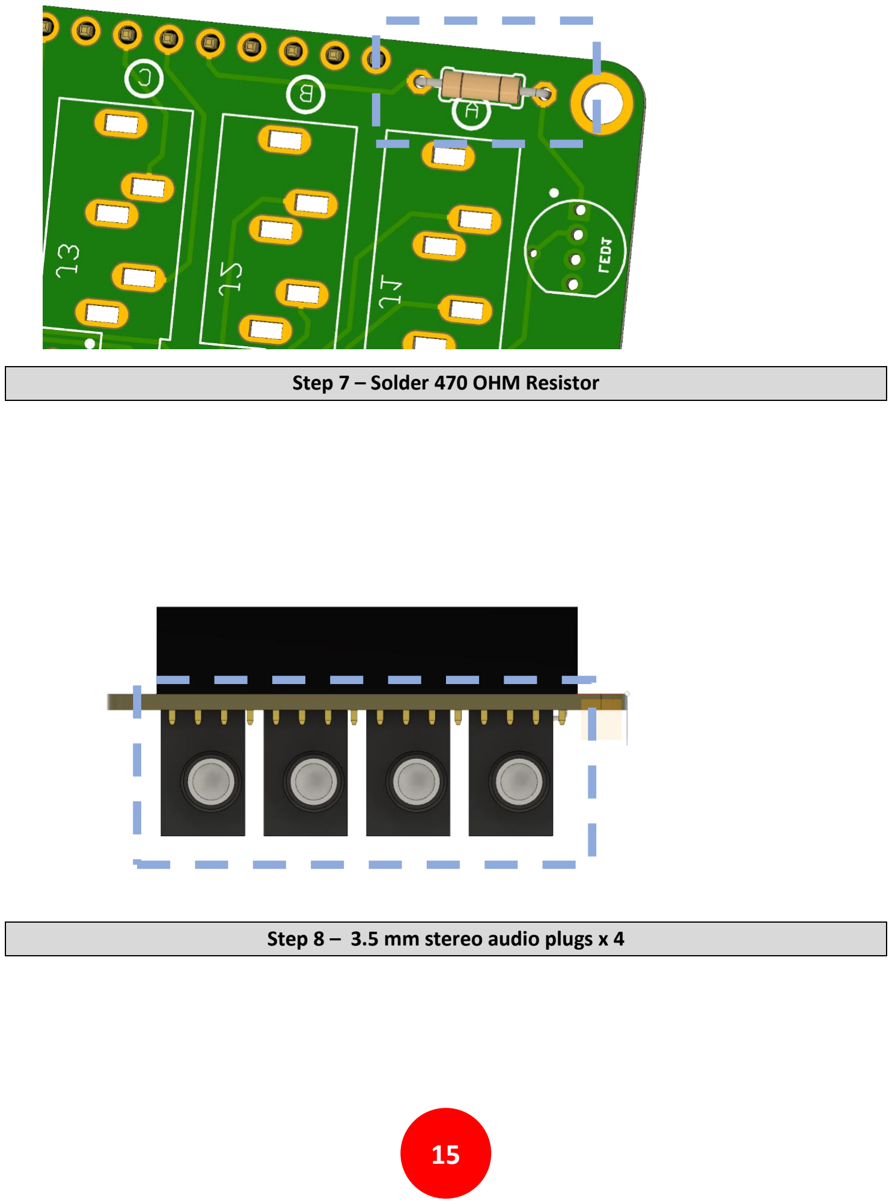
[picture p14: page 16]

15

Step 7 – Solder 470 OHM Resistor
Step 8 – 3.5 mm stereo audio plugs x 4

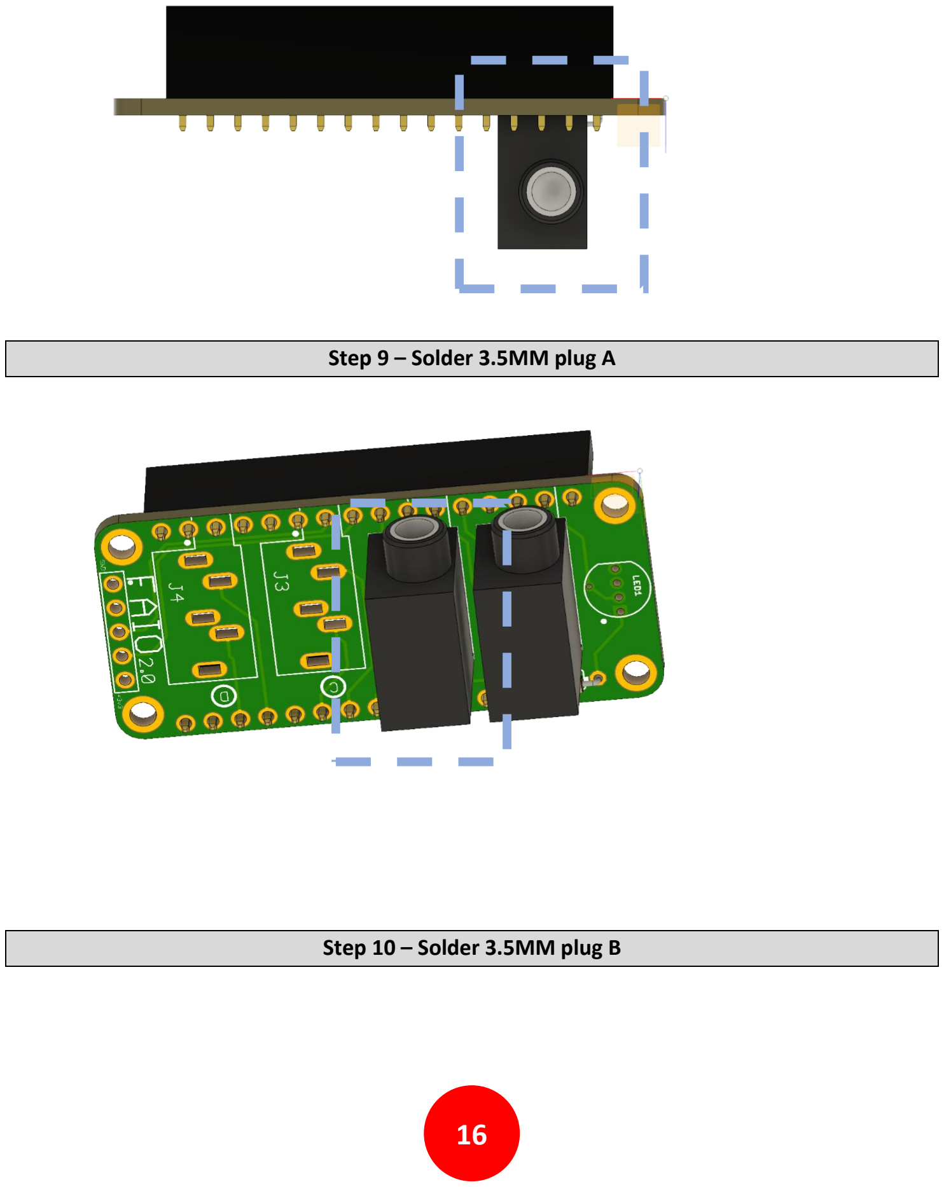
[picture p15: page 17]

16

Step 9 – Solder 3.5MM plug A
Step 10 – Solder 3.5MM plug B

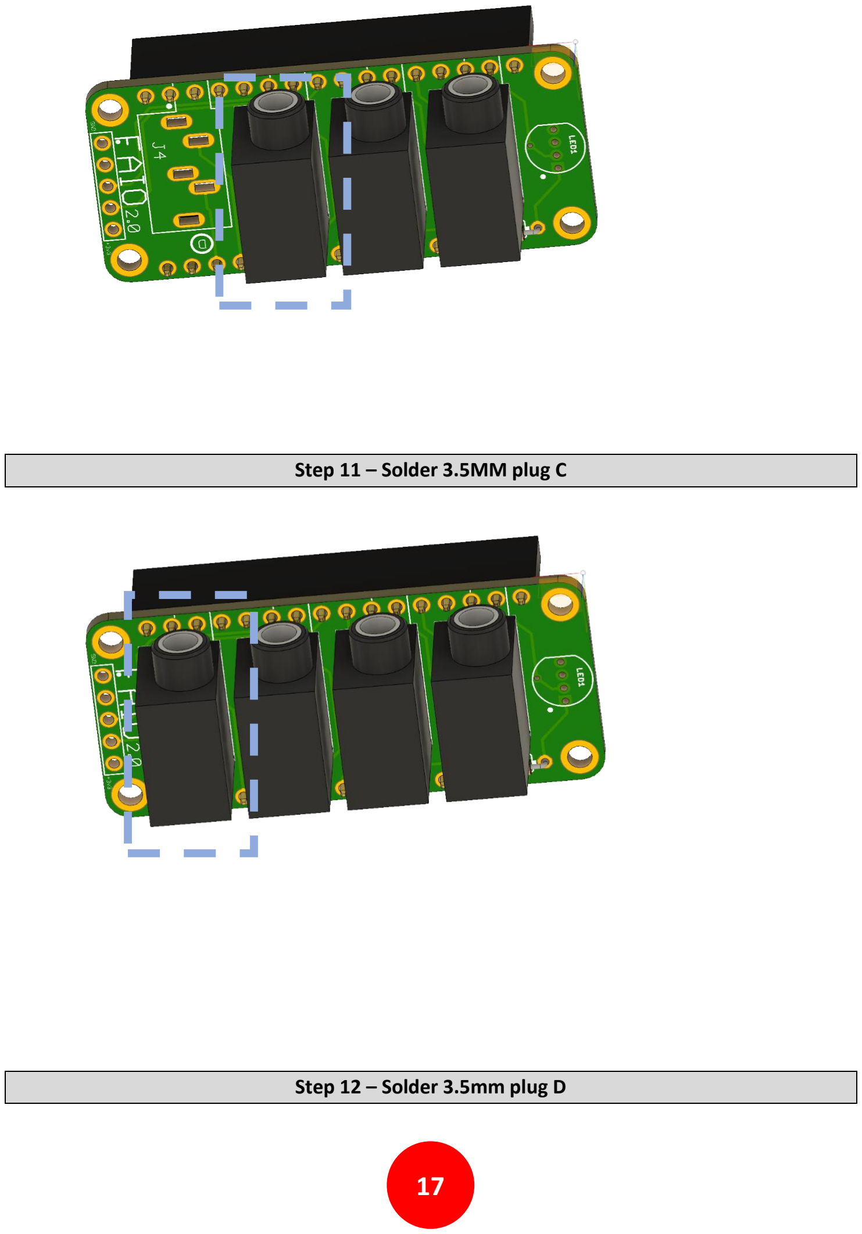
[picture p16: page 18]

17

Step 11 – Solder 3.5MM plug C
Step 12 – Solder 3.5mm plug D

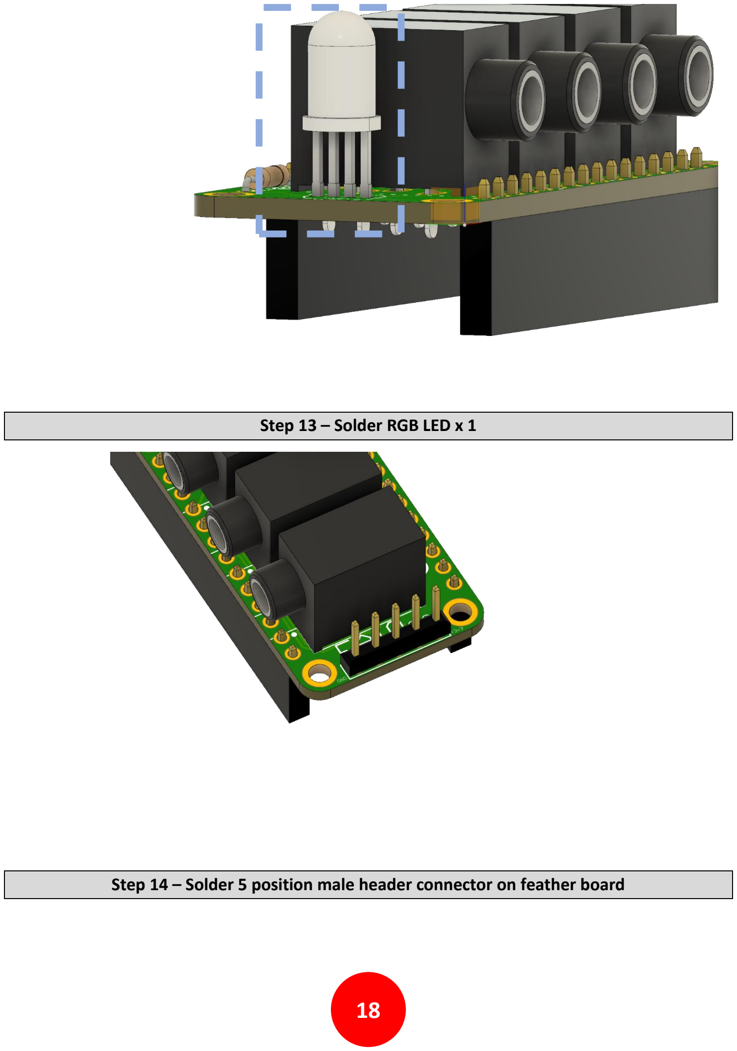
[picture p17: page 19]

18

Step 13 – Solder RGB LED x 1
Step 14 – Solder 5 position male header connector on feather board

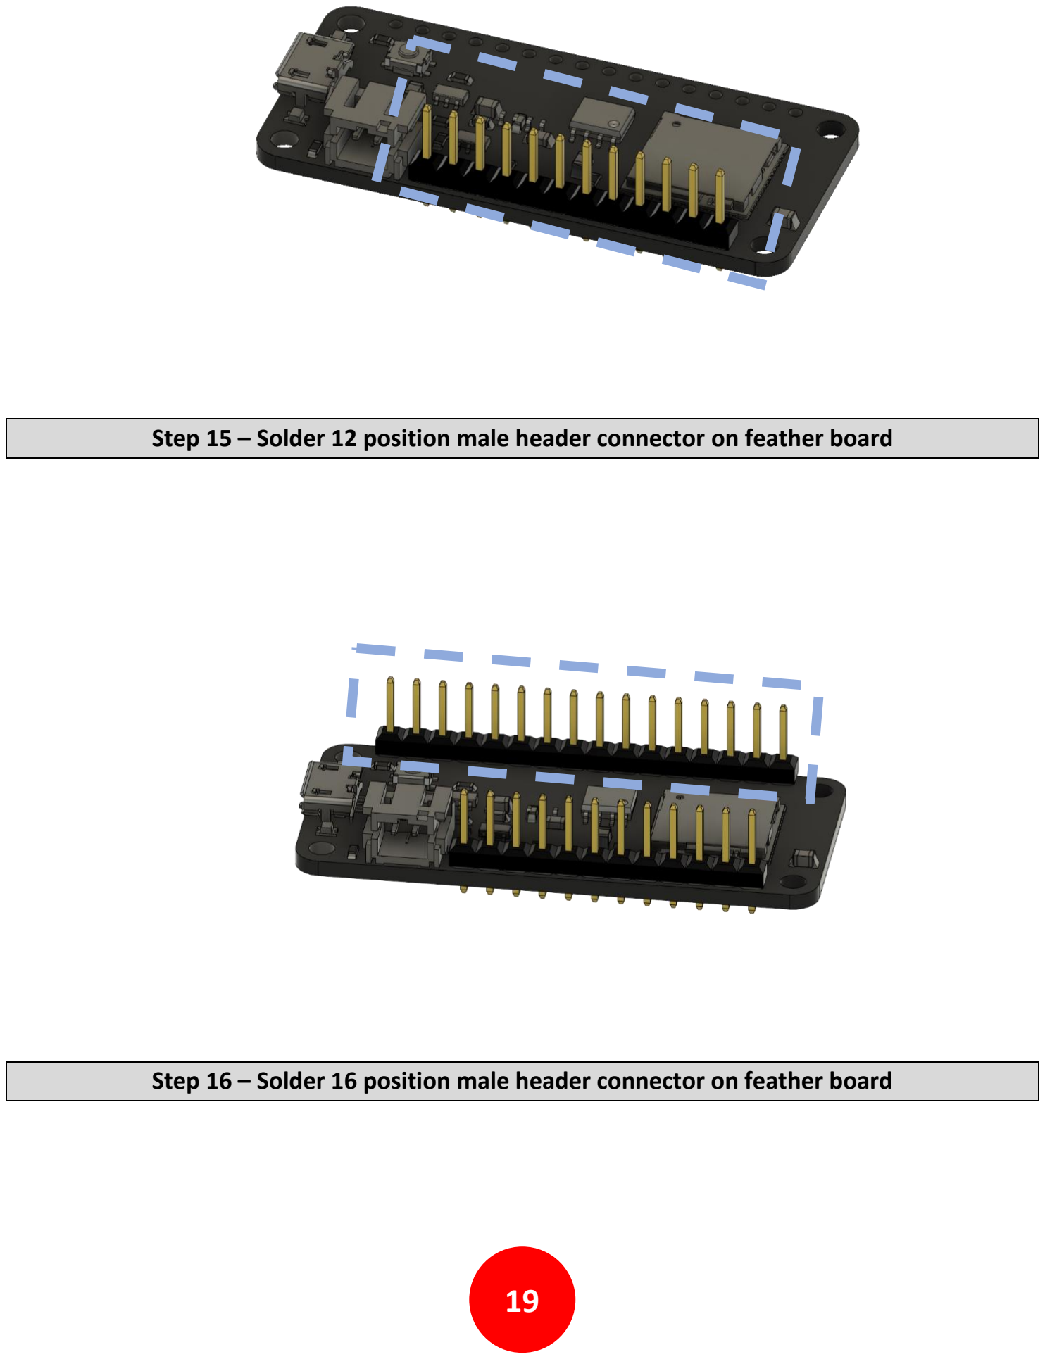
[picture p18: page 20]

19

Step 15 – Solder 12 position male header connector on feather board
Step 16 – Solder 16 position male header connector on feather board

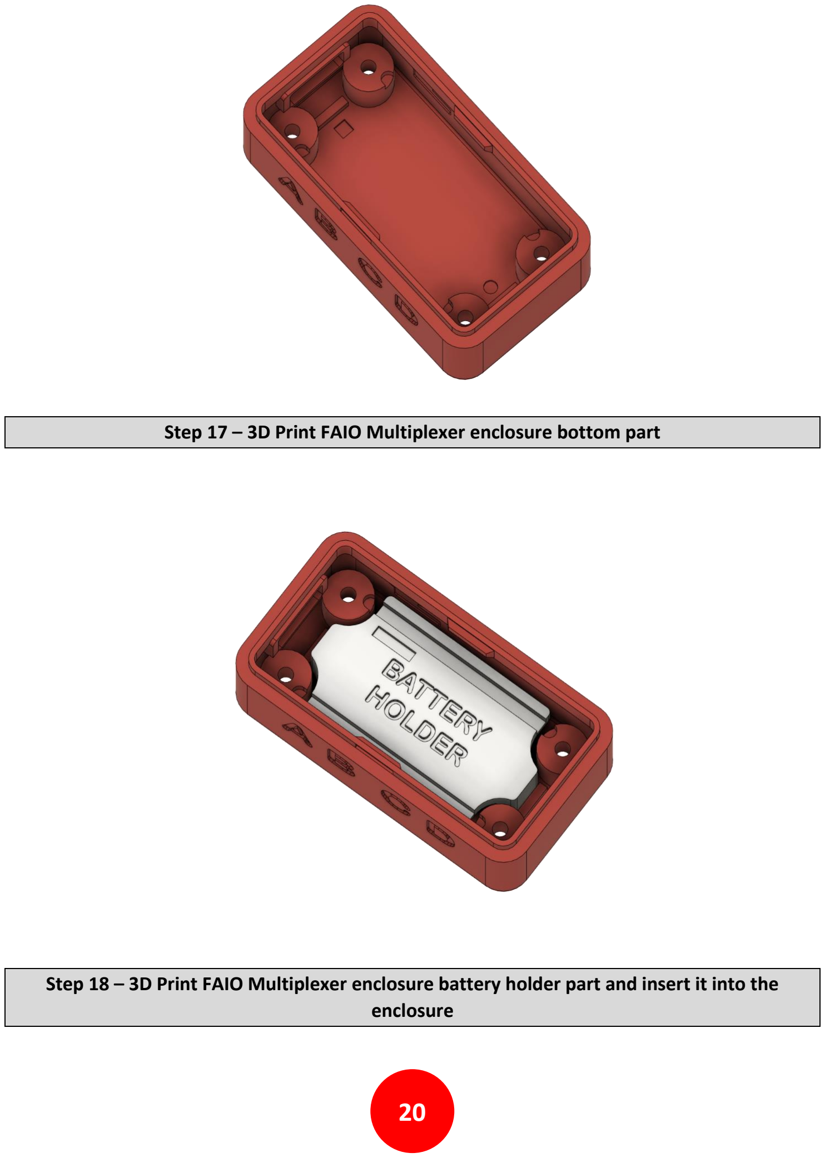
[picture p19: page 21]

20

Step 17 – 3D Print FAIO Multiplexer enclosure bottom part
Step 18 – 3D Print FAIO Multiplexer enclosure battery holder part and insert it into the enclosure

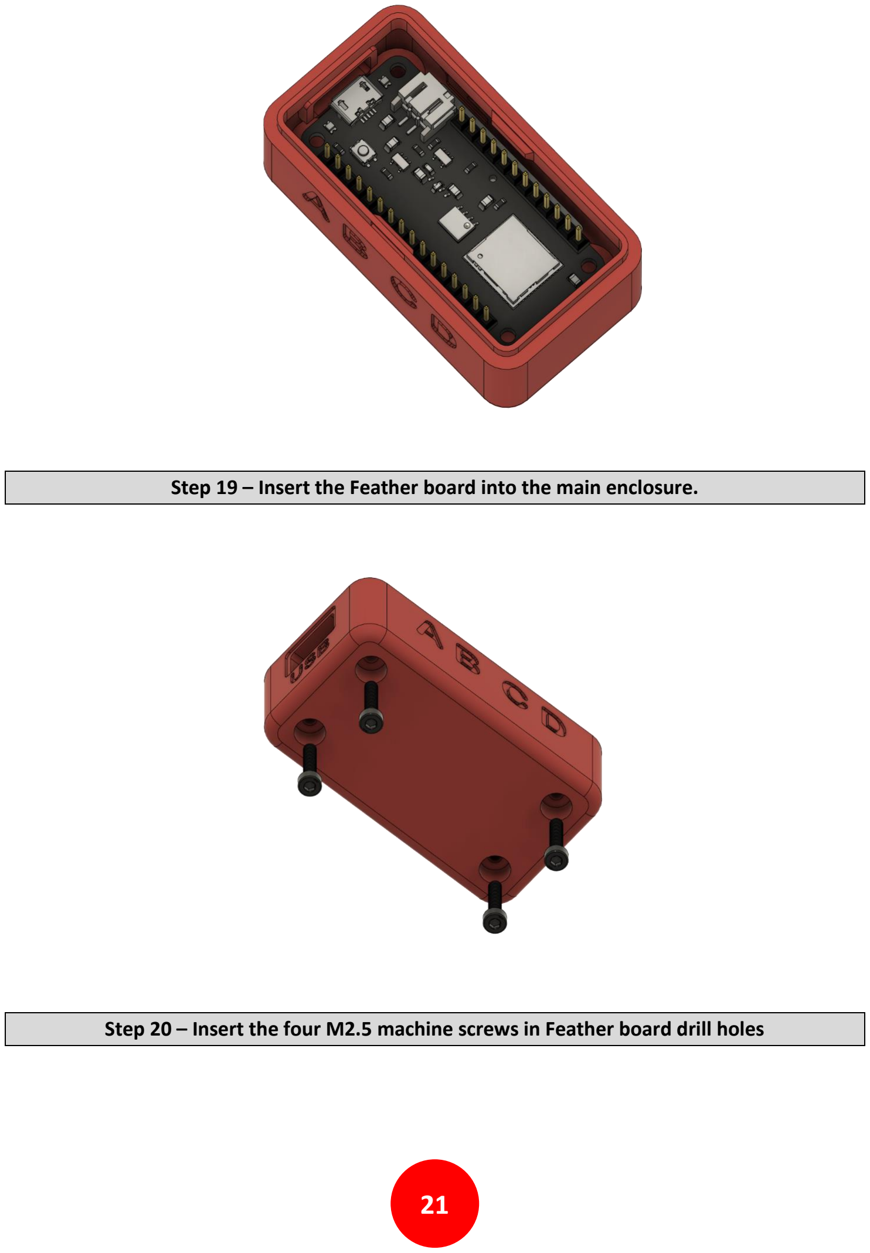
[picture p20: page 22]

21

Step 19 – Insert the Feather board into the main enclosure.
Step 20 – Insert the four M2.5 machine screws in Feather board drill holes

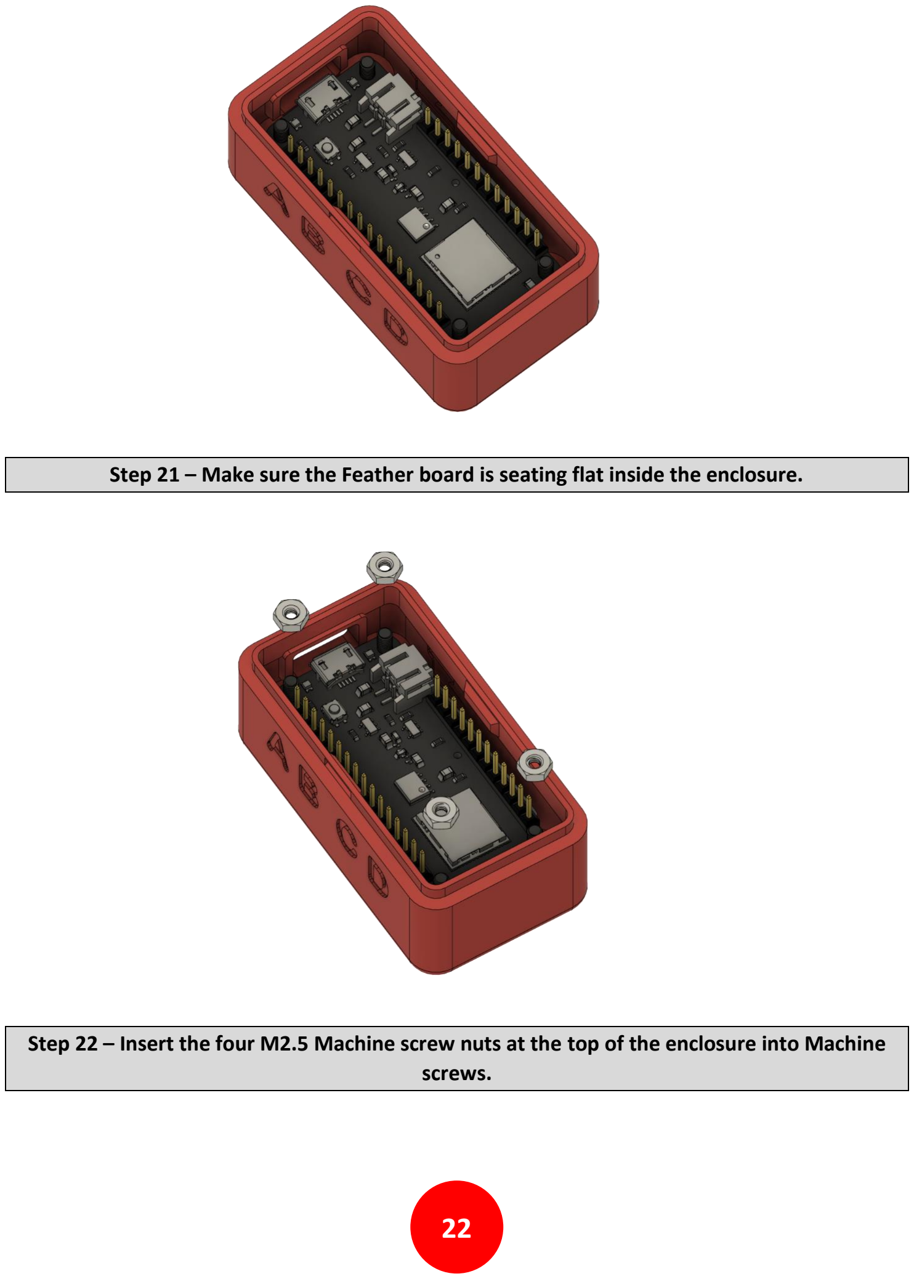
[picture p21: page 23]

22

Step 21 – Make sure the Feather board is seating flat inside the enclosure.
Step 22 – Insert the four M2.5 Machine screw nuts at the top of the enclosure into Machine screws.

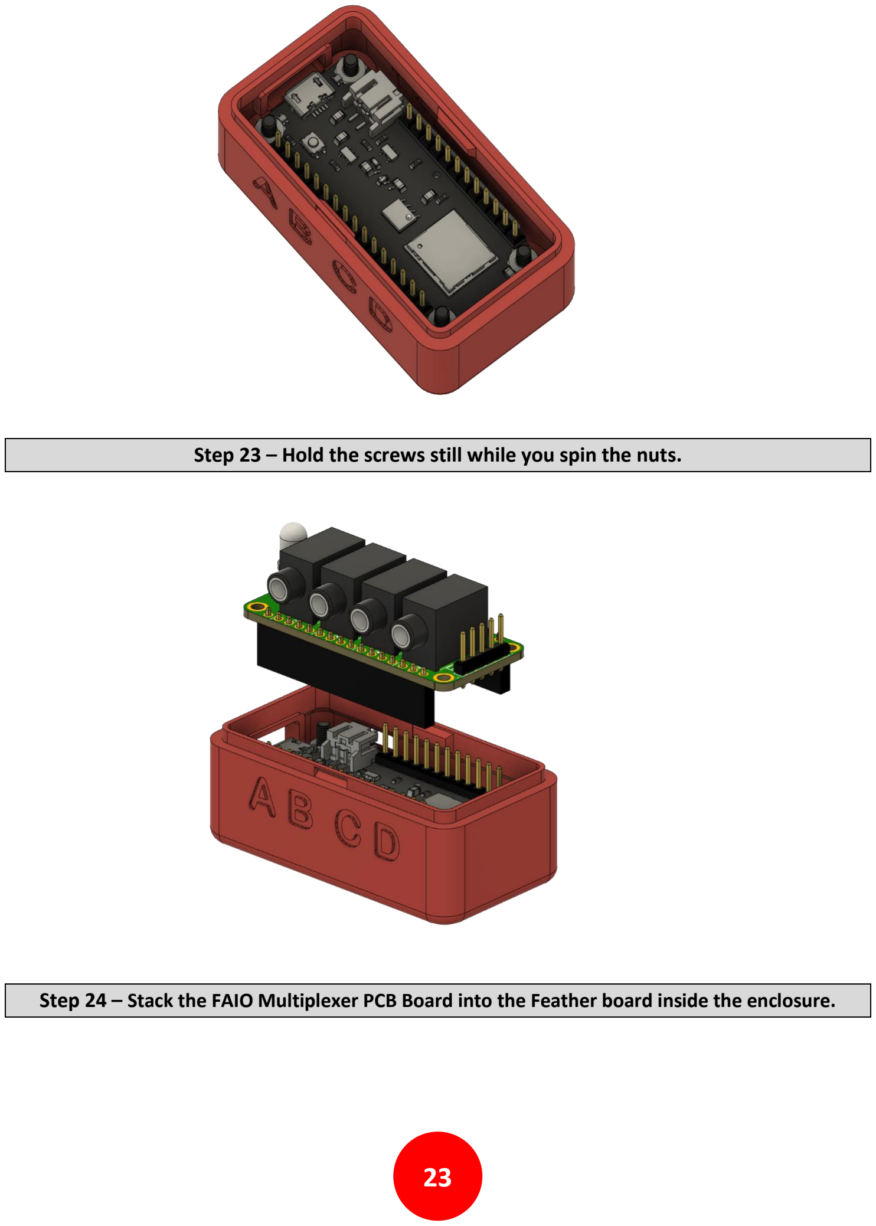
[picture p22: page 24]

23

Step 23 – Hold the screws still while you spin the nuts.
Step 24 – Stack the FAIO Multiplexer PCB Board into the Feather board inside the enclosure.

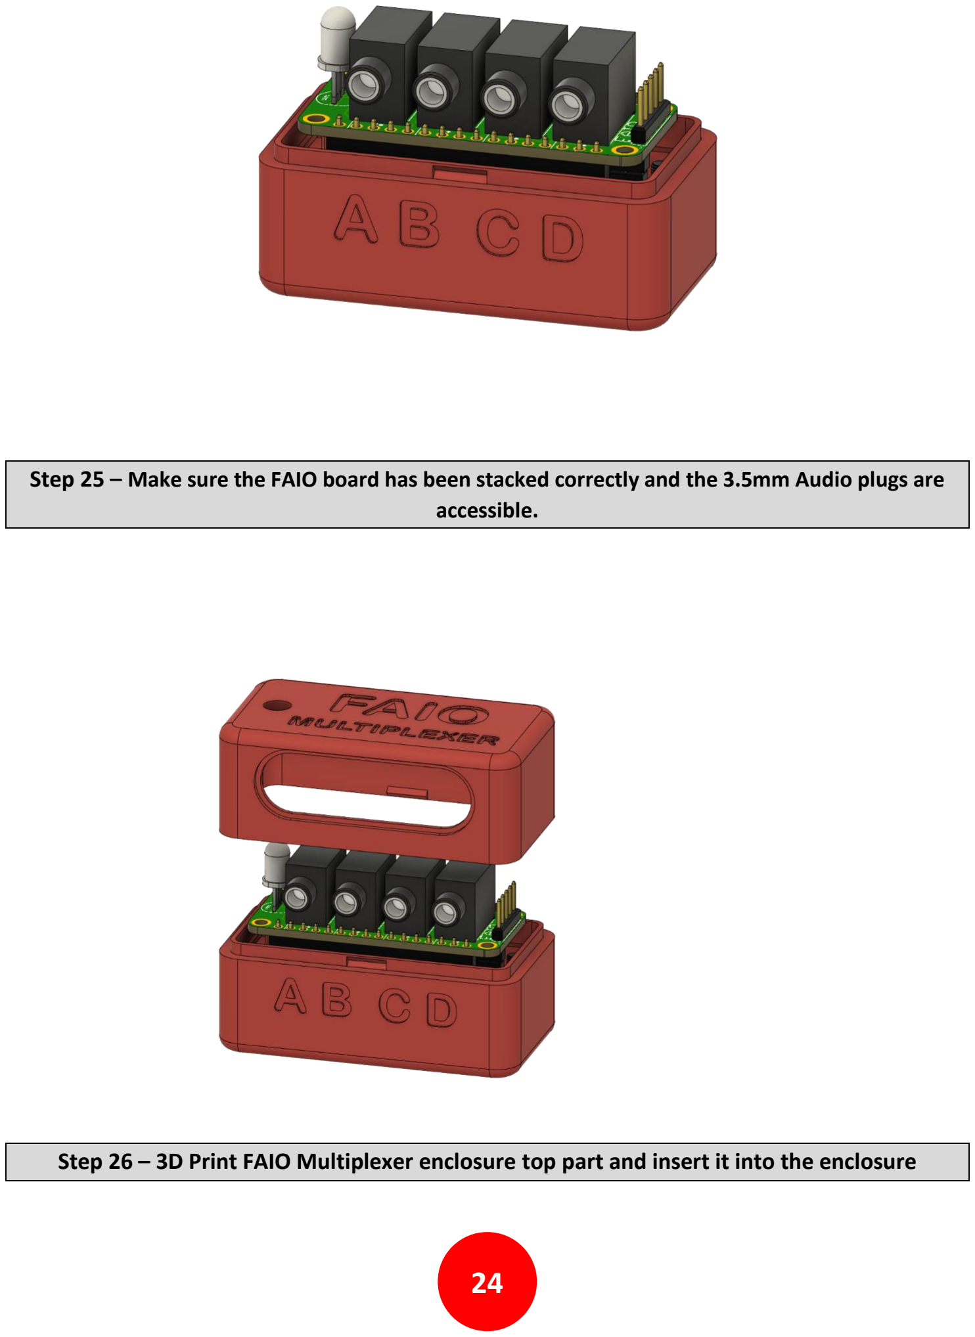
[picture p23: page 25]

24

Step 25 – Make sure the FAIO board has been stacked correctly and the 3.5mm Audio plugs are accessible.
Step 26 – 3D Print FAIO Multiplexer enclosure top part and insert it into the enclosure

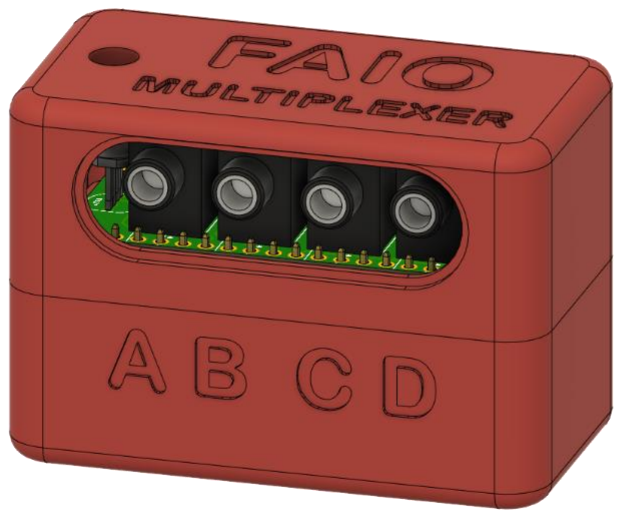
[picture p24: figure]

25

Step 27 – That’s it! Your FAIO Multiplexer is fully assembled and ready to use.

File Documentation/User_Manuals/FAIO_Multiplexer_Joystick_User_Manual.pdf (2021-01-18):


# FAIO MULTIPLEXER JOYSTICK USER MANUAL

What if you could have a switch interface that would let you perform many actions using only 4 switches?

### Version 1.1

https://github.com/milador/FAIO_Multiplexer

1

## Contents

Usage | 2
Mode 1 | 2
Mode 2 | 3
Settings Mode | 3
Customization | 3

2

## Usage

The FAIO Multiplexer Joystick can used in different configurations based on the needs of the end user. The FAIO Multiplexer hardware can be used along different software as input device for multiple devices. The hardware allows you connect up to four input 3.5mm adaptive switches which are marked A,B,C,D on both circuit board and the enclosure.

All four switches can be used as inputs when short pressed and switch D can be used to change the operation mode when it’s pressed and hold for more than 2 seconds. Table 1 represents all the possible actions for switches and their corresponding led feedback.

Button | XAC | Action | Color
A | X1 | Short press | Blue
B | X2 | Short press | Yellow
C | A | Short press | Green
D | B | Short press | Red
D | | Long Press | Mode Led Color
Table 1: FAIO Multiplexer Joystick switch actions and feedback

The device will blink two times in the color of operating mode when the initialization process is completed and will stay in that color. The led will blink momentary in color of the switch pressed as represented in Table 1 and the led color will go back to the color of operating mode. The mode can only change when switch D is pressed and hold for 2 seconds.

The Joystick version is great for usage along computer or for gaming purposes as it’s able to simulate an USB joystick device. The Joystick version can operate in different modes as it’s represented in Table 2.

Mode Number | Mode | Color
1 | Mode 1 | Teal
2 | Mode 2 | Pink
3 | Settings | Orange
Table 2: FAIO Multiplexer Joystick modes

Mode 1
The mode 1 will operate similar to a four key joystick which is great for playing computer-based games or XBOX games through XAC.
Button | Action | Color | Result
A | Short press | Blue | Press button 1
B | Short press | Yellow | Press button 2
C | Short press | Green | Press button 3
D | Short press | Red | Press button 4
D | Long Press | Mode Led Color | Change operating mode
Table 3: FAIO Multiplexer Joystick mode 1 actions

The time between each switch press actions is calculated by switch reaction levels which can be changed in settings mode or manually through the software. The switch reaction time variable is used to calculate the reaction time for each of the 10 levels as represented in Table 4.

3

SWITCH_REACTION_TIME 50

The switch reaction time variable is set to 50 by default.

Level | 10 | 9 | 8 | 7 | 6 | 5 | 4 | 3 | 2 | 1
Time (ms) | 1*50 | 2*50 | 3*50 | 4*50 | 5*50 | 6*50 | 7*50 | 8*50 | 9*50 | 10*50

Table 4: FAIO Multiplexer Joystick switch reaction time

Mode 2
The mode 2 will operate similar to mode but it allows you to press other four joystick buttons.
Button | Action | Color | Result
A | Short press | Blue | Press button 5
B | Short press | Yellow | Press button 6
C | Short press | Green | Press button 7
D | Short press | Red | Press button 8
D | Long Press | Mode Led Color | Change operating mode
Table 5: FAIO Multiplexer Joystick mode 2 actions

Settings Mode
The settings mode is used to change the reaction level and reaction time using the A and B switches. The led will blink in blue when react level is increased and in red when reaction level is decreased. The number of led blinks indicate new reaction level. The led will blink 10 times when it reaches maximum or minimum reaction levels.
Button | Action | Color | Result
A | Short press | Blue | Increase Reaction level (Decrease Reaction time)
B | Short press | Red | Decrease Reaction level (Increase Reaction time)
D | Long Press | Mode Led Color | Change operating mode
Table 6: FAIO Multiplexer Joystick settings actions

There are total of 10 levels and the switch reaction times and morse reaction times can be calculated using Tablets 7.

Level | 10 | 9 | 8 | 7 | 6 | 5 | 4 | 3 | 2 | 1
Time (ms) | 1*50 | 2*50 | 3*50 | 4*50 | 5*50 | 6*50 | 7*50 | 8*50 | 9*50 | 10*50

Table 7: FAIO Multiplexer Joystick reaction time

### Customization

The FAIO Multiplexer joystick can easily be customized by changing the value of variables at the beginning of FAIO Multiplexer USB software. The following variables can be changed for customization purposes:

#define SWITCH_REACTION_TIME 50

4

The switch reaction time multiplier between each switch action

#define SWITCH_MODE_CHANGE_TIME 2000

The time that switch D needs to be hold in ms to perform mode change action

#define LED_BRIGHTNESS 150

The brightness of led for mode indication

#define LED_ACTION_BRIGHTNESS 150

The brightness of led for action indication

#define JOYSTICK_DEADZONE 5

The deadzone value of the joystick module

#define JOYSTICK_ENABLED false

This will enable usage of analog joystick module when it’s available

//Switch properties

const switchStruct switchProperty[] {

{1,"X1",1,5,5},

{2,"X2",2,6,3},

{3,"A",3,7,1},

{4,"B",4,8,6}

};

The values of third and fourth columns can be changed to have different joystick button press actions and the fifth column can be changed for customization of led feedback.

//Settings Action properties

const settingsActionStruct settingsProperty[] {

{1,"Increase Reaction",5}, | //{1=Increase Reaction,5=blue}
{2,"Decrease Reaction",6}, | //{2=Decrease Reaction,6=red}
{3,"Max Reaction",1}, | //{3=Max Reaction,1=green}
{4,"Min Reaction",1} | //{4=Min Reaction,1=green}

};

The third column can be changed for customization of led feedback.

//Mode properties

5

const modeStruct modeProperty[] {

{1,"Mode 1",8},

{2,"Mode 2",2},

{4,"Settings",4}

};

The third column can be changed for customization of led feedback.

const colorStruct colorProperty[] {

{1,"Green",{0,50,0}},

{2,"Pink",{50,00,20}},

{3,"Yellow",{50,50,0}},

{4,"Orange",{50,20,0}},

{5,"Blue",{0,0,50}},

{6,"Red",{50,0,0}},

{7,"Purple",{50,0,50}},

{8,"Teal",{0,128,128}}

};

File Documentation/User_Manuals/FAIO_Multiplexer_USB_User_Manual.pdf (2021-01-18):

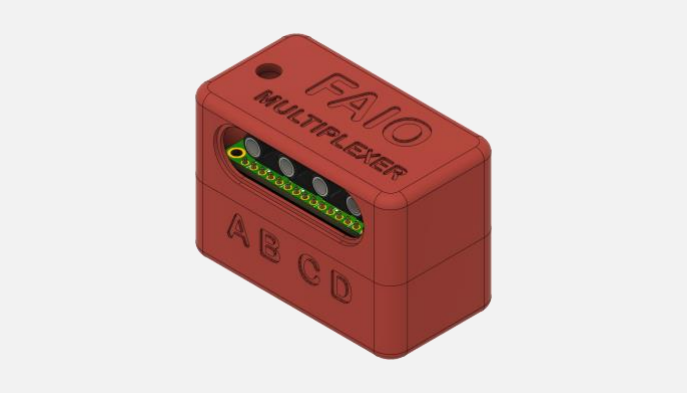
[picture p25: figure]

# FAIO MULTIPLEXER USB USER MANUAL

What if you could have a switch interface that could that would let you perform many actions using only 4 switches?

### Version 1.1

https://github.com/milador/FAIO_Multiplexer

1

## Contents

Usage | 2
Keyboard Switch mode | 2
Morse Keyboard Mode | 3
Morse Mouse Mode | 4
Settings Mode | 4
Customization | 5

2

## Usage

The FAIO Multiplexer USB can used in different configurations based on the needs of the end user. The FAIO Multiplexer hardware can be used along different software as input device for multiple devices. The hardware allows you connect up to four input 3.5mm adaptive switches which are marked A,B,C,D on both circuit board and the enclosure.

All four switches can be used as inputs when short pressed and switch D can be used to change the operation mode when it’s pressed and hold for more than 2 seconds. Table 1 represents all the possible actions for switches and their corresponding led feedback.

Button | Action | Color
A | Short press | Blue
B | Short press | Red
C | Short press | Green
D | Short press | Yellow
D | Long Press | Mode Led Color
Table 1: FAIO Multiplexer USB switch actions and feedback

The device will blink two times in the color of operating mode when the initialization process is completed and will stay in that color. The led will blink momentary in color of the switch pressed as represented in Table 1 and the led color will go back to the color of operating mode. The mode can only change when switch D is pressed and hold for 2 seconds.

The USB version is great for usage along computer or smartphone devices as it’s able to simulate a USB mouse or USB keyboard device. The USB version can operate in different modes as it’s represented in Table 2.

Mode Number | Mode | Color
1 | Keyboard Switch | Teal
2 | Morse Keyboard | Purple
3 | Morse Mouse | Pink
4 | Settings | Orange
Table 2: FAIO Multiplexer USB modes

Keyboard Switch mode
The Keyboard Switch will operate similar to a four key keyboard which is great for using as switches for your computer or smartphone device through features such as Switch access and it can also be used to play computer games via WASD format keyboard.
Button | Action | Color | Result
A | Short press | Blue | Send ‘a’ keystroke
B | Short press | Red | Send ‘b’ keystroke
C | Short press | Green | Send ‘c’ keystroke
D | Short press | Yellow | Send ‘d’ keystroke
D | Long Press | Mode Led Color | Change operating mode
Table 3: FAIO Multiplexer USB switch actions

3

The time between each switch press actions is calculated by switch reaction levels which can be changed in settings mode or manually through the software. The switch reaction time variable is used to calculate the reaction time for each of the 10 levels as represented in Table 4.

SWITCH_REACTION_TIME 50

The switch reaction time variable is set to 50 by default.

Level | 10 | 9 | 8 | 7 | 6 | 5 | 4 | 3 | 2 | 1
Time (ms) | 1*50 | 2*50 | 3*50 | 4*50 | 5*50 | 6*50 | 7*50 | 8*50 | 9*50 | 10*50

Table 4: FAIO Multiplexer USB switch reaction time

Morse Keyboard Mode
This mode is used to convert morse code to keystrokes via 2 switches. The first switch acts as dot and second switch acts as dash as explained in Table 5.
Button | Action | Color | Result
A | Short press | Blue | Send ‘.’ To morse stack
B | Short press | Red | Send ‘-’ To morse stack
D | Long Press | Mode Led Color | Change operating mode
Table 5: FAIO Multiplexer USB morse keyboard mode

The conversion of morse code combination to characters is done in software based on the static variables in the beginning of the code. These values can be customized based on your needs.

MORSE_TIMEOUT 1000

MORSE_REACTION_TIME 10

The timeout is the time in ms that is measured since last switch action to perform the morse conversation and send the result as keystroke. The time by default is set to 1 second ( 1000 ms ) which means the device will convert the morse code combinations if switch A and B (Dot , Dash ) are not pressed for 1 second.

The reaction time is the multiplier for time between each dot and dash. The higher reaction level means lower reaction time. The reaction levels can be changed using switches in the settings mode but it’s also possible to change the morse reaction time multiplier in the code. Table 6 can be used to understand the morse reaction time calculation.

Lev el | 10 | 9 | 8 | 7 | 6 | 5 | 4 | 3 | 2 | 1
Time (ms) | (1.5^1)* 10 | (1.5^2)* 10 | (1.5^3)* 10 | (1.5^4)* 10 | (1.5^5)* 10 | (1.5^6)* 10 | (1.5^7)* 10 | (1.5^8)* 10 | (1.5^9)* 10 | (1.5^10)* 10

Table 6: FAIO Multiplexer USB morse reaction time

The table of morse code combinations can be found on EasyMorse (https://github.com/milador/EasyMorse) project github repository.

4

Morse Mouse Mode
This mode is used to convert morse code to mouse via 2 switches. The first switch acts as dot and second switch acts as dash as explained in Table 7.
Button | Action | Color | Result
A | Short press | Blue | Send ‘.’ To morse stack
B | Short press | Red | Send ‘-’ To morse stack
D | Long Press | Mode Led Color | Change operating mode
Table 7: FAIO Multiplexer USB morse mouse mode

This mode users the morse timeout value and morse reaction time to convert morse code combinations to mouse actions similar to morse keyboard mode. The table of morse code combinations can be found on EasyMorse (https://github.com/milador/EasyMorse) project github repository. The conversion table is represented in Table 8 in addition.

Morse code | Result
- Move Up
-- | Move Down
.. | Move Left
... | Move Right
.- | Left Click
.-- | Right Click
..- | Double Left Click
..-- | Double Right Click
-. | Left Click & Hold/Release
-.. | Right Click & Hold/Release
Table 8: FAIO Multiplexer USB morse mouse code conversion table

The mouse move actions are fixed in terms of number of pixels that cursor can be moved for each morse code combination , but there is mouse move multiplier variable available in the software that allows you to customize the mouse move behavior based on your needs.

MOUSE_MOVE_MULTI 2

The mouse move multiplier variable is set to 2 by default.

Settings Mode
The settings mode is used to change the reaction level and reaction time using the A and B switches. The led will blink in blue when react level is increased and in red when reaction level is decreased. The number of led blinks indicate new reaction level. The led will blink 10 times when it reaches maximum or minimum reaction levels.
Button | Action | Color | Result
A | Short press | Blue | Increase Reaction level (Decrease Reaction time)
B | Short press | Red | Decrease Reaction level (Increase Reaction time)
D | Long Press | Mode Led Color | Change operating mode
Table 9: FAIO Multiplexer USB settings mode

There are total of 10 levels and the switch reaction times and morse reaction times can be calculated using Tablets 10 and 11.

5

Level | 10 | 9 | 8 | 7 | 6 | 5 | 4 | 3 | 2 | 1
Time (ms) | 1*50 | 2*50 | 3*50 | 4*50 | 5*50 | 6*50 | 7*50 | 8*50 | 9*50 | 10*50

Table 10: FAIO Multiplexer USB switch reaction time

Lev el | 10 | 9 | 8 | 7 | 6 | 5 | 4 | 3 | 2 | 1
Time (ms) | (1.5^1)* 10 | (1.5^2)* 10 | (1.5^3)* 10 | (1.5^4)* 10 | (1.5^5)* 10 | (1.5^6)* 10 | (1.5^7)* 10 | (1.5^8)* 10 | (1.5^9)* 10 | (1.5^10)* 10

Table 11: FAIO Multiplexer USB morse reaction time

### Customization

The FAIO Multiplexer USB can easily be customized by changing the value of variables at the beginning of FAIO Multiplexer USB software. The following variables can be changed for customization purposes:

#define MORSE_TIMEOUT 1000

The time of no activity which is used as flag to convert the morse combination to keystroke

#define MORSE_REACTION_TIME 10

The morse reaction time multiplier between each dot and dash actions

#define MOUSE_MOVE_MULTI 2

The morse mouse move multiplier variable

#define SWITCH_REACTION_TIME 50

The switch reaction time multiplier between each switch action

#define SWITCH_MODE_CHANGE_TIME 2000

The time that switch D needs to be hold in ms to perform mode change action

#define LED_BRIGHTNESS 150

The brightness of led for mode indication

#define LED_ACTION_BRIGHTNESS 150

The brightness of led for action indication

//Switch properties

const switchStruct switchProperty[] {

{1,"DOT",'a',5,1}, | //{1=dot,"DOT",'a',5=blue,1=1xMORSE_REACTION}
{2,"DASH",'b',6,3}, | //{2=dash,"DASH",'b',6=red,3=3xMORSE_REACTION}
{3,"",'c',1,1}, | //{3,"",'c',1=green,1=1xMORSE_REACTION}

6

{4,"",'d',3,1} | //{4,"",'d',3=yellow,1=1xMORSE_REACTION}

};

The values of third column can be changed to different characters and the fourth column can be changed for customization of led feedback.

//Settings Action properties

const settingsActionStruct settingsProperty[] {

{1,"Increase Reaction",5}, | //{1=Increase Reaction,5=blue}
{2,"Decrease Reaction",6}, | //{2=Decrease Reaction,6=red}
{3,"Max Reaction",1}, | //{3=Max Reaction,1=green}
{4,"Min Reaction",1} | //{4=Min Reaction,1=green}

};

The third column can be changed for customization of led feedback.

//Mode properties

const modeStruct modeProperty[] {

{1,"Keyboard Switch",8},

{2,"Morse Keyboard",7},

{3,"Morse Mouse",2},

{4,"Settings",4}

};

The third column can be changed for customization of led feedback.

const colorStruct colorProperty[] {

{1,"Green",{0,50,0}},

{2,"Pink",{50,00,20}},

{3,"Yellow",{50,50,0}},

{4,"Orange",{50,20,0}},

{5,"Blue",{0,0,50}},

{6,"Red",{50,0,0}},

7

{7,"Purple",{50,0,50}},

{8,"Teal",{0,128,128}}

};

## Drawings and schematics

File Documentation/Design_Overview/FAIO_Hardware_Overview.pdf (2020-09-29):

## FAIO Hardware Overview

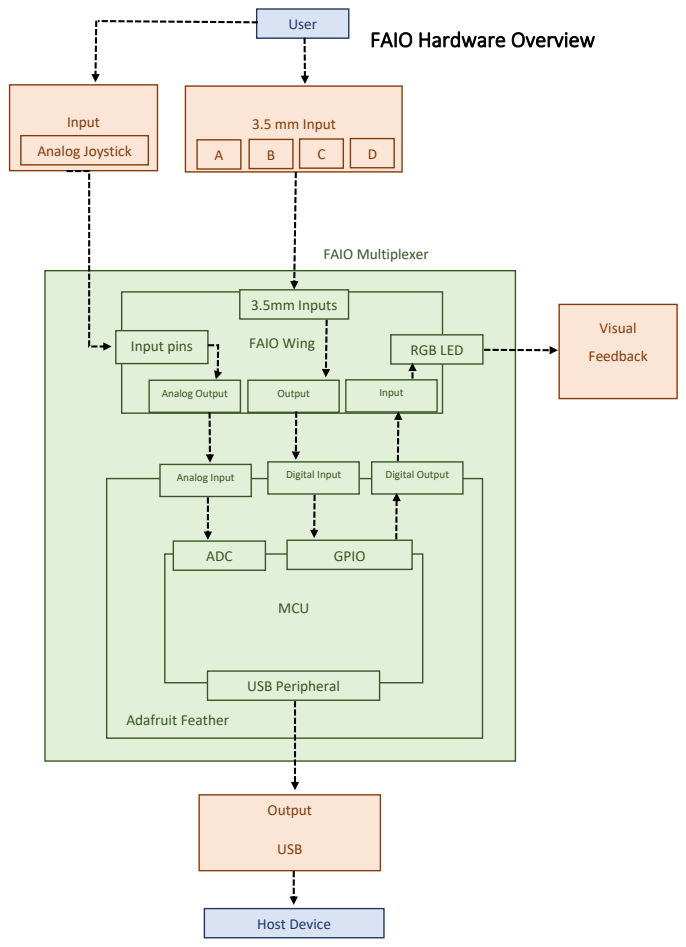
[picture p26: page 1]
User; 3.5 mm Input; FAIO Wing; RGB LED; Visual; Feedback; MCU; USB Peripheral; 3.5mm Inputs; Output; USB; Input; Analog Joystick; Input pins; ADC; GPIO; Analog Output; Analog Input; Digital Input; Digital Output; Host Device; FAIO Multiplexer; Adafruit Feather

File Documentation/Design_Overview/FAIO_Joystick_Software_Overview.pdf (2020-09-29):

## FAIO Joystick Software Overview

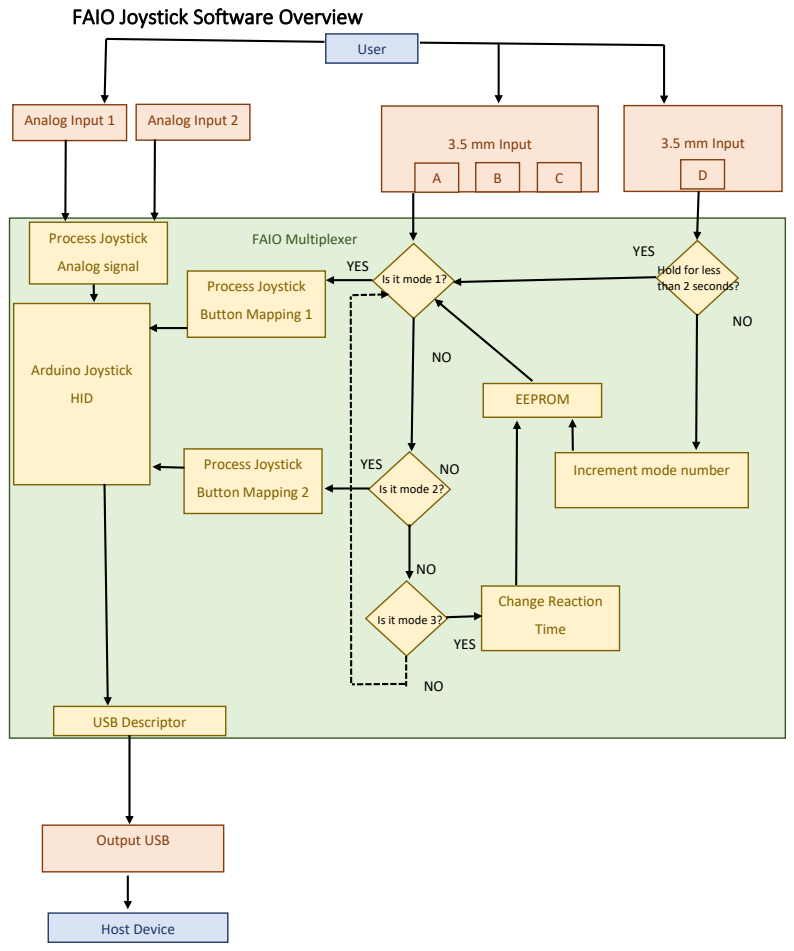
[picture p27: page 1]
User; 3.5 mm Input; USB Descriptor; Output USB; Analog Input 1; Process Joystick; Button Mapping 1; Host Device; FAIO Multiplexer; Analog Input 2; EEPROM; Button Mapping 2; Arduino Joystick; HID; Change Reaction; Time; YES; Analog signal

YES
Hold for less
than 2 seconds?

Is it mode 1?

Increment mode number

Is it mode 2?

Is it mode 3?

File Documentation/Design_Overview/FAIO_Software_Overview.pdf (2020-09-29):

## FAIO Software Overview

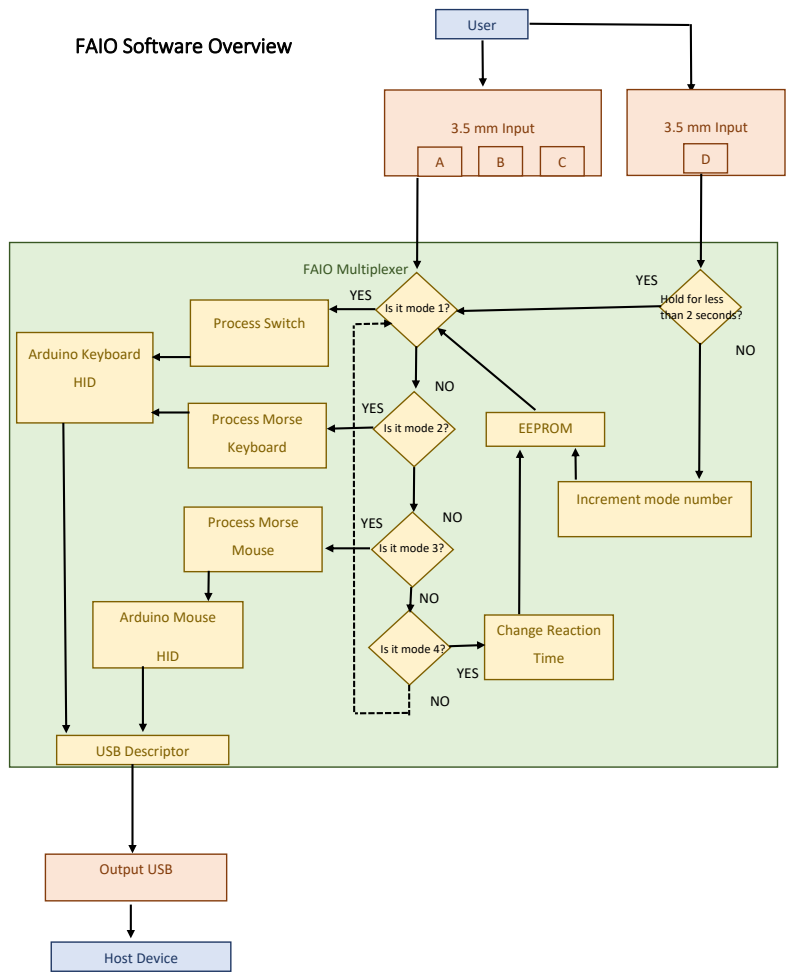
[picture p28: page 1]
User; 3.5 mm Input; USB Descriptor; Output USB; Process Switch; Host Device; FAIO Multiplexer; Is it mode 2?; EEPROM; Process Morse; Keyboard; Mouse; Arduino Keyboard; HID; Arduino Mouse; Change Reaction; Time; YES

YES
Hold for less
than 2 seconds?

Is it mode 1?

Increment mode number

Is it mode 3?

Is it mode 4?

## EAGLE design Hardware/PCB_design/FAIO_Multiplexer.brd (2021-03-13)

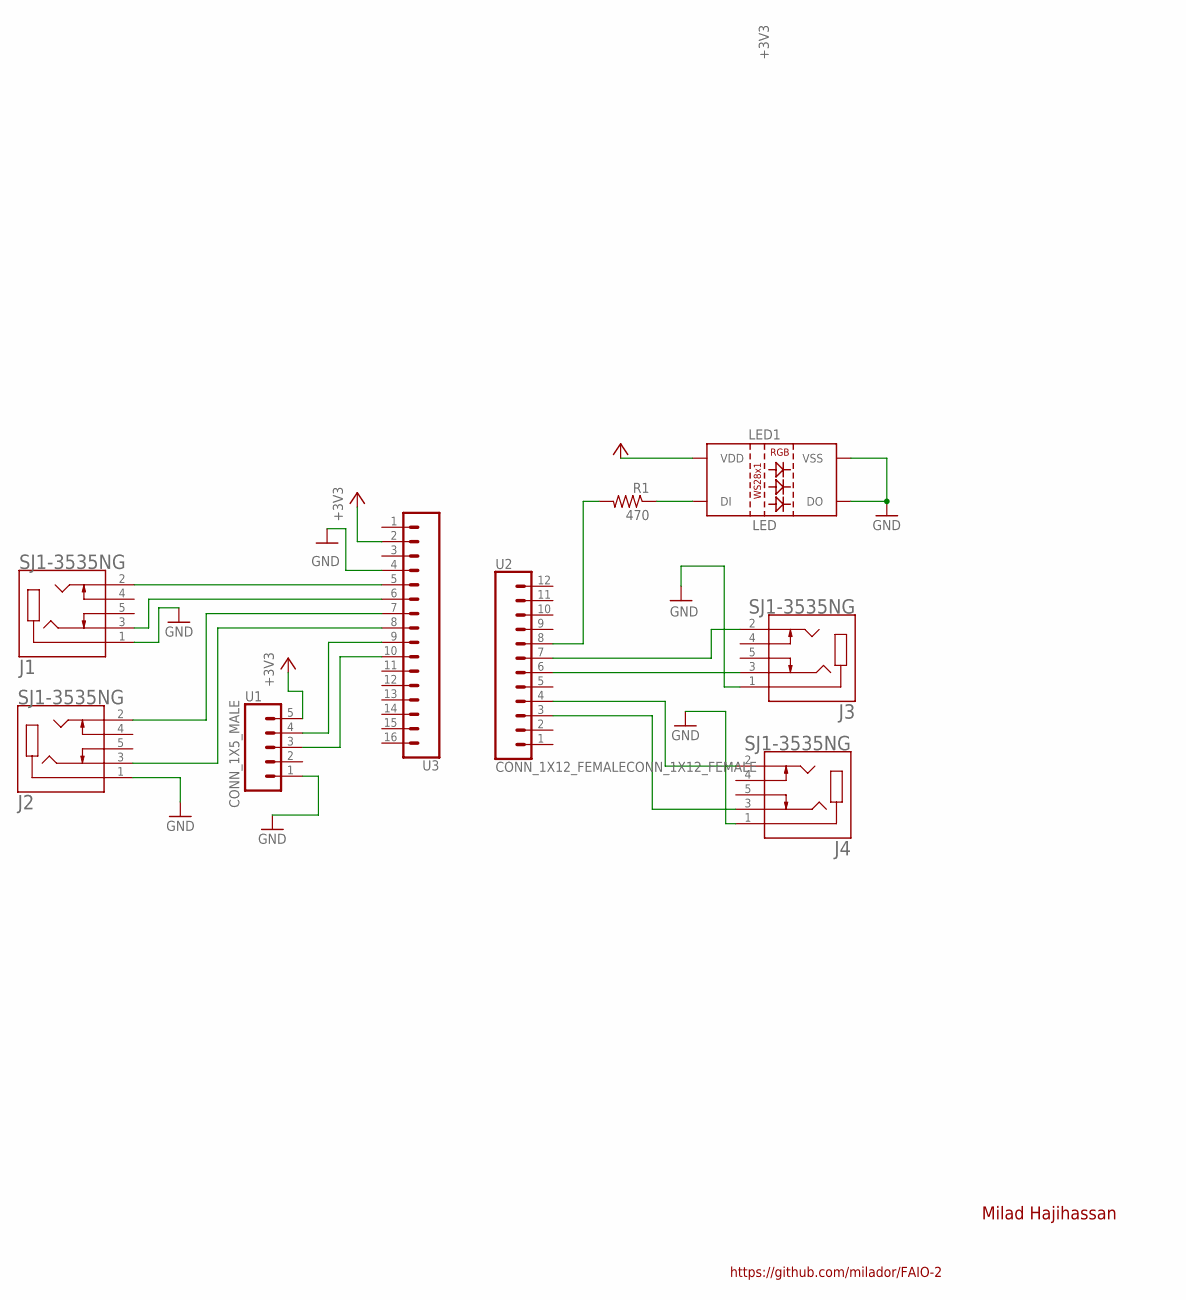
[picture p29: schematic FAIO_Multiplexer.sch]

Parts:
J1, J2, J3, J4: SJ1-3535NG; CUI_SJ1-3535NG
LED1: LED; NEOPIXELS-5MM
R1: 470; 0204/7
U1: CONN_1X5_MALE; CONN_1X5
U2: CONN_1X12_FEMALECONN_1X12_FEMALE; CONN_1X12
U3: CONN_1X16_FEMALECONN_1X16_FEMALE; CONN_1X16

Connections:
+3V3: LED1.2 (VDD), U1.5, U3.2
GND: J1.1, J2.1, J3.1, J4.1, LED1.3 (VSS), LED1.4 (DO), U1.1, U3.4
unnamed: J3.3, U2.6
unnamed: J3.2, U2.7
unnamed: J4.2, U2.4
unnamed: LED1.1 (DI), R1.1
unnamed: J4.3, U2.3
unnamed: R1.2, U2.8
unnamed: U1.4, U3.9
unnamed: J1.2, U3.5
unnamed: J1.3, U3.6
unnamed: J2.2, U3.7
unnamed: U1.3, U3.10
unnamed: J2.3, U3.8

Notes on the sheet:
https://github.com/milador/FAIO-2
Milad Hajihassan

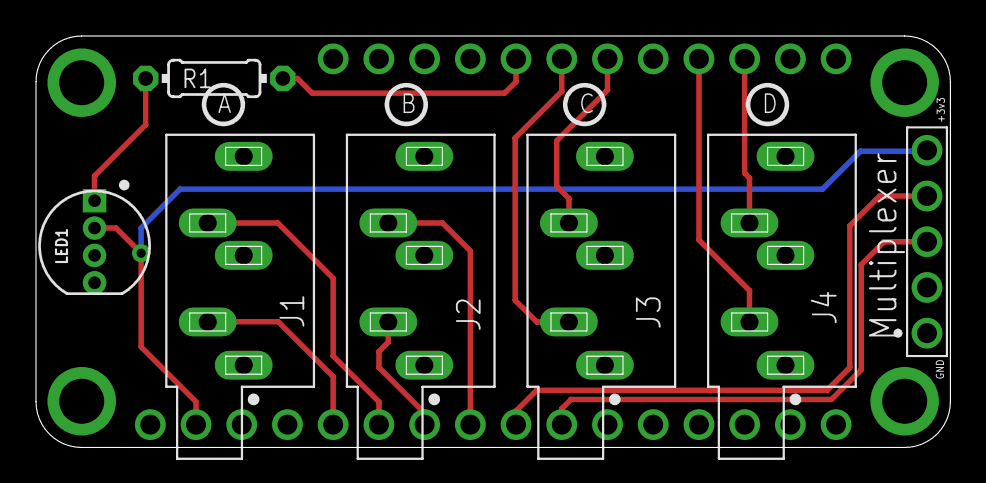
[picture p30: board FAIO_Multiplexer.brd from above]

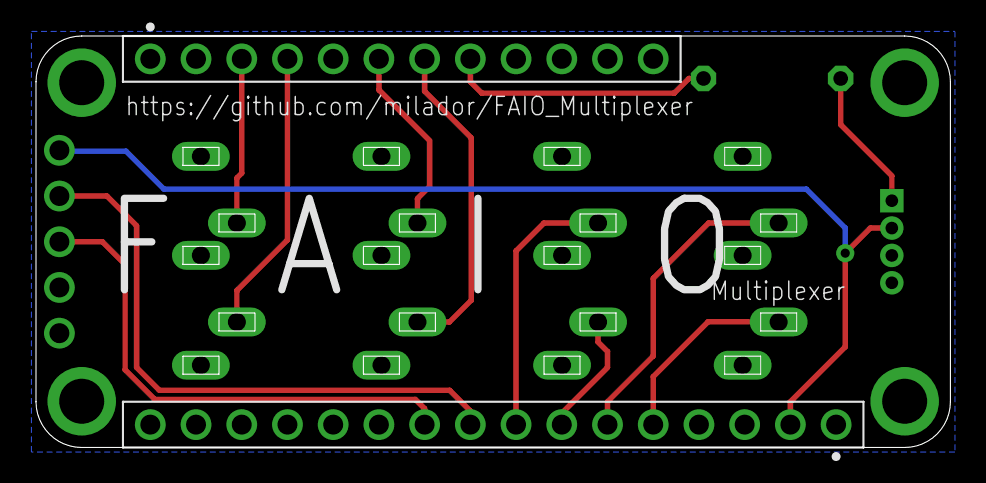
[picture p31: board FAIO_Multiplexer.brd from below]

Board: 2 copper layers, 50.8 x 22.9 mm, 9 parts (2 on the bottom side), 14 nets.

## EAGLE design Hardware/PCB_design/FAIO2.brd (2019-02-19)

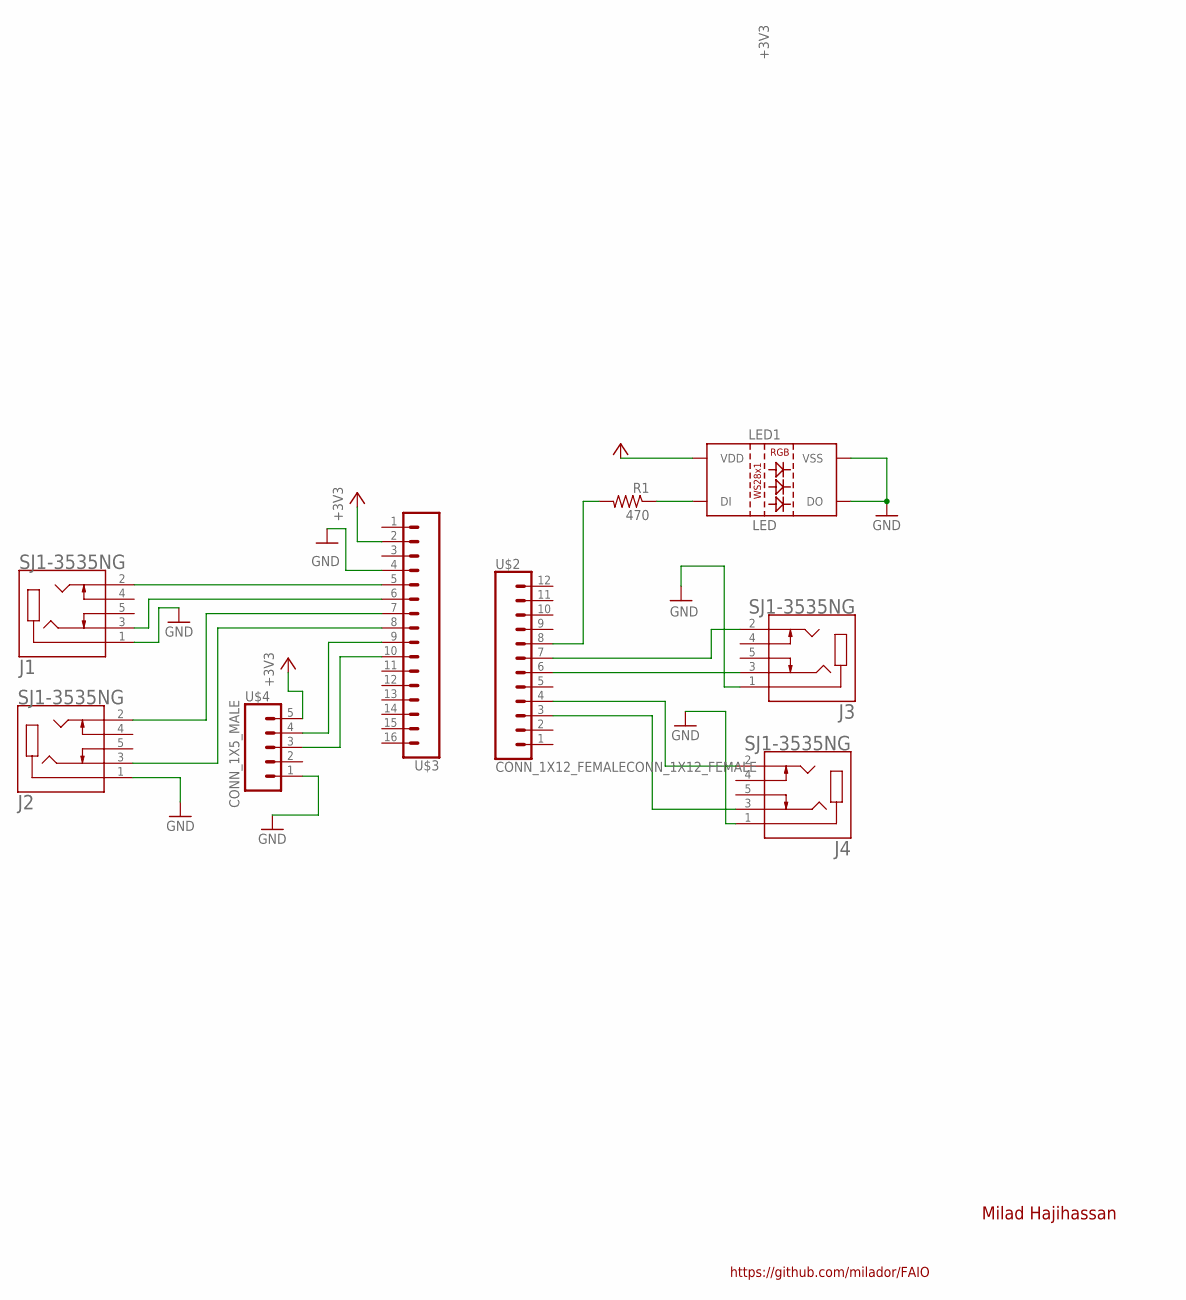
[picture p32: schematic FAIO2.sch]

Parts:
J1, J2, J3, J4: SJ1-3535NG; CUI_SJ1-3535NG
LED1: LED; NEOPIXELS-5MM
R1: 470; 0204/7
U$2: CONN_1X12_FEMALECONN_1X12_FEMALE; CONN_1X12
U$3: CONN_1X16_FEMALECONN_1X16_FEMALE; CONN_1X16
U$4: CONN_1X5_MALE; CONN_1X5

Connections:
+3V3: LED1.2 (VDD), U$3.2, U$4.5
GND: J1.1, J2.1, J3.1, J4.1, LED1.3 (VSS), LED1.4 (DO), U$3.4, U$4.1
unnamed: J3.3, U$2.6
unnamed: J3.2, U$2.7
unnamed: J4.2, U$2.4
unnamed: LED1.1 (DI), R1.1
unnamed: J4.3, U$2.3
unnamed: R1.2, U$2.8
unnamed: U$3.9, U$4.4
unnamed: J1.2, U$3.5
unnamed: J1.3, U$3.6
unnamed: J2.2, U$3.7
unnamed: U$3.10, U$4.3
unnamed: J2.3, U$3.8

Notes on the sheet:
https://github.com/milador/FAIO
Milad Hajihassan

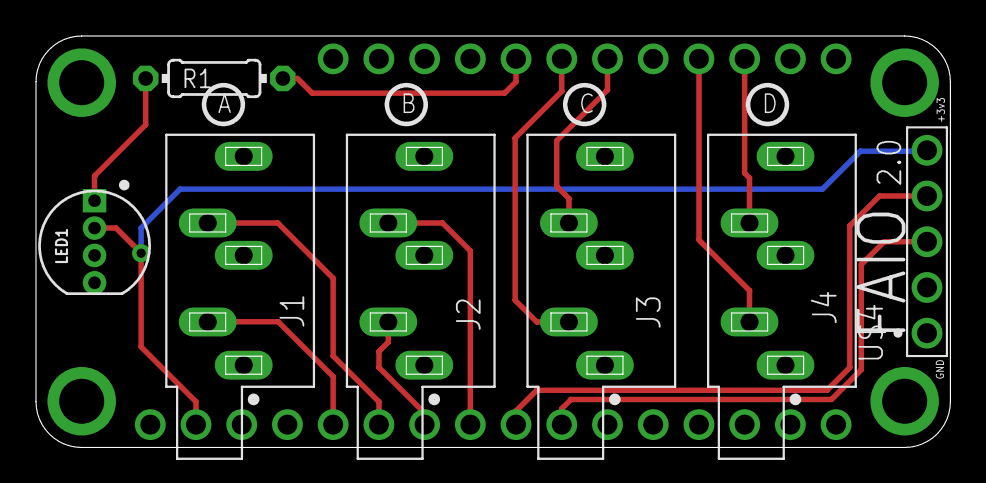
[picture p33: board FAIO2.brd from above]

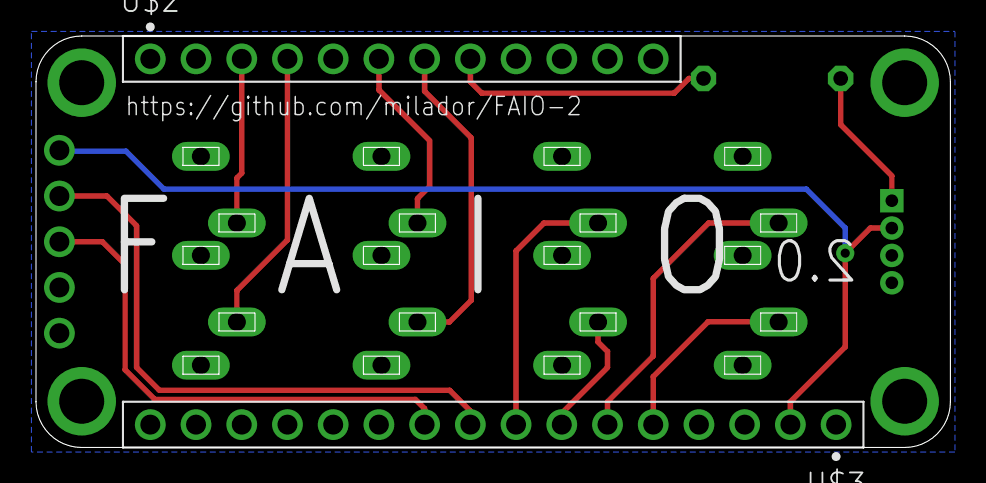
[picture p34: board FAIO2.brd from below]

Board: 2 copper layers, 50.8 x 22.9 mm, 9 parts (2 on the bottom side), 14 nets.

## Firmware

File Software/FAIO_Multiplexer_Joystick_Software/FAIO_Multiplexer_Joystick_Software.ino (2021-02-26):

//FFFFFFFFFFFFFFFFFFFFFF               AAA               IIIIIIIIII     OOOOOOOOO           222222222222222                 000000000     
//F::::::::::::::::::::F              A:::A              I::::::::I   OO:::::::::OO        2:::::::::::::::22             00:::::::::00   
//F::::::::::::::::::::F             A:::::A             I::::::::I OO:::::::::::::OO      2::::::222222:::::2          00:::::::::::::00 
//FF::::::FFFFFFFFF::::F            A:::::::A            II::::::IIO:::::::OOO:::::::O     2222222     2:::::2         0:::::::000:::::::0
//  F:::::F       FFFFFF           A:::::::::A             I::::I  O::::::O   O::::::O                 2:::::2         0::::::0   0::::::0
//  F:::::F                       A:::::A:::::A            I::::I  O:::::O     O:::::O                 2:::::2         0:::::0     0:::::0
//  F::::::FFFFFFFFFF            A:::::A A:::::A           I::::I  O:::::O     O:::::O              2222::::2          0:::::0     0:::::0
//  F:::::::::::::::F           A:::::A   A:::::A          I::::I  O:::::O     O:::::O         22222::::::22           0:::::0 000 0:::::0
//  F:::::::::::::::F          A:::::A     A:::::A         I::::I  O:::::O     O:::::O       22::::::::222             0:::::0 000 0:::::0
//  F::::::FFFFFFFFFF         A:::::AAAAAAAAA:::::A        I::::I  O:::::O     O:::::O      2:::::22222                0:::::0     0:::::0
//  F:::::F                  A:::::::::::::::::::::A       I::::I  O:::::O     O:::::O     2:::::2                     0:::::0     0:::::0
//  F:::::F                 A:::::AAAAAAAAAAAAA:::::A      I::::I  O::::::O   O::::::O     2:::::2                     0::::::0   0::::::0
//FF:::::::FF              A:::::A             A:::::A   II::::::IIO:::::::OOO:::::::O     2:::::2       222222        0:::::::000:::::::0
//F::::::::FF             A:::::A               A:::::A  I::::::::I OO:::::::::::::OO      2::::::2222222:::::2 ......  00:::::::::::::00 
//F::::::::FF            A:::::A                 A:::::A I::::::::I   OO:::::::::OO        2::::::::::::::::::2 .::::.    00:::::::::00   
//FFFFFFFFFFF           AAAAAAA                   AAAAAAAIIIIIIIIII     OOOOOOOOO          22222222222222222222 ......      000000000    

//FAIO_Multiplexer Joystick Software
//FAIO_Multiplexer_Joystick_Software
//Written by: Milad Hajihassan
//Version 1.0 (12/4/2020)
//Github Link: https://github.com/milador/FAIO_Multiplexer

#include "Joystick.h"
#include <StopWatch.h>
#include <math.h>
#include <Adafruit_NeoPixel.h>

//Use FlashStorage library for M0 Boards and EEPROM for Atmega32U4 boards
#if defined(ARDUINO_SAMD_FEATHER_M0)
#include <FlashStorage.h>
#elif defined(__AVR_Atmega32U4__)
#include <EEPROM.h>
#endif


//Can be changed based on the needs of the users 
#define FIXED_SPEED_LEVEL 6
#define FIXED_DELAY 30
#define JOYSTICK_DEADZONE 5
#define JOYSTICK_ENABLED false
#define SWITCH_REACTION_TIME 50                                       //Minimum time for each switch action ( level 10 : 1x50 =50ms , level 1 : 10x50=500ms )
#define SWITCH_MODE_CHANGE_TIME 2000                                  //How long to hold switch 4 to change mode 

#define LED_BRIGHTNESS 150                                             //The mode led color brightness which is always on ( Use a low value to decrease power usage )
#define LED_ACTION_BRIGHTNESS 150                                      //The action led color brightness which can be a higher value than LED_BRIGHTNESS


//Define Switch pins
#define LED_PIN 12

#define SWITCH1_PIN A0
#define SWITCH2_PIN A2
#define SWITCH3_PIN 11
#define SWITCH4_PIN 6

//Define Joystick pins
#define X_JOYSTICK_PIN A4
#define Y_JOYSTICK_PIN A5  


// Variable Declaration

//Declare switch state variables for each switch
int switch1State;
int switch2State;
int switch3State;
int switch4State;

//Declare joystick variables 
int xJoystick;
int yJoystick;

//Stopwatches array used to time switch presses
StopWatch switch4TimeWatcher[1];


//Declare Switch variables for settings 
int switchConfigured;
int switchReactionTime;
int switchReactionLevel;
int switchMode;


//Declare Flash storage variables 
#if defined(ARDUINO_SAMD_FEATHER_M0)
FlashStorage(switchConfiguredFlash, int);
FlashStorage(switchReactionLevelFlash, int);
FlashStorage(switchModeFlash, int);
#endif


//RGB LED Color code structure 

struct rgbColorCode {
    int r;    // red value 0 to 255
    int g;   // green value
    int b;   // blue value
 };

//Color structure 
typedef struct { 
  uint8_t colorNumber;
  String colorName;
  rgbColorCode colorCode;
} colorStruct;

 //Mode structure 
typedef struct { 
  uint8_t modeNumber;
  String modeName;
  uint8_t modeColorNumber;
} modeStruct;


 //Switch structure 
typedef struct { 
  uint8_t switchNumber;
  String switchButtonName;
  uint8_t switchMode1ButtonNumber;
  uint8_t switchMode2ButtonNumber;
  uint8_t switchColorNumber;
} switchStruct;


 //Settings Action structure 
typedef struct { 
  uint8_t settingsActionNumber;
  String settingsActionName;
  uint8_t settingsActionColorNumber;
} settingsActionStruct;

//Color properties 
const colorStruct colorProperty[] {
    {1,"Green",{0,50,0}},
    {2,"Pink",{50,00,20}},
    {3,"Yellow",{50,50,0}},    
    {4,"Orange",{50,20,0}},
    {5,"Blue",{0,0,50}},
    {6,"Red",{50,0,0}},
    {7,"Purple",{50,0,50}},
    {8,"Teal",{0,128,128}}       
};

//Switch properties 
const switchStruct switchProperty[] {
    {1,"X1",1,5,5},
    {2,"X2",2,6,3},
    {3,"A",3,7,1},
    {4,"B",4,8,6}
};

//Settings Action properties 
const settingsActionStruct settingsProperty[] {
    {1,"Increase Reaction",5},                             //{1=Increase Reaction,5=blue}
    {2,"Decrease Reaction",6},                             //{2=Decrease Reaction,6=red}
    {3,"Max Reaction",1},                                  //{3=Max Reaction,1=green}
    {4,"Min Reaction",1}                                   //{4=Min Reaction,1=green}
};

//Mode properties 
const modeStruct modeProperty[] {
    {1,"Mode 1",8},
    {2,"Mode 2",2},
    {4,"Settings",4}
};


//Setup NeoPixel LED
Adafruit_NeoPixel ledPixels = Adafruit_NeoPixel(1, LED_PIN, NEO_GRB + NEO_KHZ800);


//Defining the joystick REPORT_ID and profile type
Joystick_ Joystick(JOYSTICK_DEFAULT_REPORT_ID, 
  JOYSTICK_TYPE_JOYSTICK, 8, 0,
  true, true, false, 
  false, false, false,
  false, false, 
  false, false, false);   

void setup() {

  ledPixels.begin();                                                           //Start NeoPixel
  Serial.begin(115200);                                                        //Start Serial
  switchSetup();
  delay(5);
  joystickSetup();
  delay(1000);
  initLedFeedback();                                                          //Led will blink in a color to show the current mode 
  delay(5);
  displayFeatureList();
  
  //Initialize the switch pins as inputs
  pinMode(SWITCH1_PIN, INPUT_PULLUP);    
  pinMode(SWITCH2_PIN, INPUT_PULLUP);   
  pinMode(SWITCH3_PIN, INPUT_PULLUP);    
  pinMode(SWITCH4_PIN, INPUT_PULLUP);  

  //Initialize the LED pin as an output
  pinMode(LED_PIN, OUTPUT);                                                      


};

void loop() {
  static int ctr;                          //Control variable to set previous status of switches 
  unsigned long timePressed;               //Time that switch one or two are pressed
  unsigned long timeNotPressed;            //Time that switch one or two are not pressed
  static int previousSw4State;             //Previous status of switch four
  
  //Update status of switch inputs
  switch1State = digitalRead(SWITCH1_PIN);
  switch2State = digitalRead(SWITCH2_PIN);
  switch3State = digitalRead(SWITCH3_PIN);
  switch4State = digitalRead(SWITCH4_PIN);


  //Update status of joystick inputs
  if(JOYSTICK_ENABLED) {
  xJoystick = analogRead(X_JOYSTICK_PIN);
  yJoystick = analogRead(Y_JOYSTICK_PIN);    
  } else {
    xJoystick = 0;
    yJoystick = 0;
  }
  
  timePressed = timeNotPressed  = 0;       //reset time counters
  if (!ctr) {                              //Set previous status of switch four 
    previousSw4State = HIGH;  
    ctr++;
  }
  //Check if switch 4 is pressed to change switch mode
  if (switch4State == LOW && previousSw4State == HIGH) {
     if (switch4State == LOW) { 
      previousSw4State = LOW; 
     }
     switch4TimeWatcher[0].stop();                                //Reset and start the timer         
     switch4TimeWatcher[0].reset();                                                                        
     switch4TimeWatcher[0].start(); 
  }
  // Switch four was released
  if (switch4State == HIGH && previousSw4State == LOW) {
    previousSw4State = HIGH;
    timePressed = switch4TimeWatcher[0].elapsed();                //Calculate the time that switch one was pressed 
    switch4TimeWatcher[0].stop();                                 //Stop the single action (dot/dash) timer and reset
    switch4TimeWatcher[0].reset();
    
    //Perform action if the switch has been hold active for specified time
    if (timePressed >= SWITCH_MODE_CHANGE_TIME){
      changeSwitchMode();                                                                
    } else if(switchMode==1 || switchMode==2) {
      joystickAction(switchMode,switch1State,switch2State,switch3State,LOW,xJoystick,yJoystick);
      delay(5);
    }
  }
  //Serial.println(switch1State);
  //Perform joystick actions based on the mode
    switch (switchMode) {
      case 1:
        joystickAction(switchMode,switch1State,switch2State,switch3State,HIGH,xJoystick,yJoystick);    //Switch mode
        break;
      case 2:
        joystickAction(switchMode,switch1State,switch2State,switch3State,HIGH,xJoystick,yJoystick);    //Switch mode
        break;
      case 3:
        settingsAction(switch1State,switch2State);                                          //Settings mode
        break;
  };
  ledPixels.show(); 
  delay(5);
}

//***DISPLAY FEATURE LIST FUNCTION***//

void displayFeatureList(void) {

  Serial.println(" ");
  Serial.println(" --- ");
  Serial.println("This is the FAIO Multiplexer Joystick firmware");
  Serial.println(" ");
  Serial.println("VERSION: 1.0 (12 April 2020)");
  Serial.println(" ");
  Serial.println(" --- ");
  Serial.println("Features: Joystick ");
  Serial.println(" --- ");
  Serial.println(" ");

}

//***RGB LED FUNCTION***//

void setLedBlink(int numBlinks, int delayBlinks, int ledColor,uint8_t ledBrightness) {
  if (numBlinks < 0) numBlinks *= -1;

      for (int i = 0; i < numBlinks; i++) {
        ledPixels.setPixelColor(0, ledPixels.Color(colorProperty[ledColor-1].colorCode.g,colorProperty[ledColor-1].colorCode.r,colorProperty[ledColor-1].colorCode.b));
        ledPixels.setBrightness(ledBrightness);
        ledPixels.show(); 
        delay(delayBlinks);
        ledPixels.setPixelColor(0, ledPixels.Color(0,0,0));
        ledPixels.setBrightness(ledBrightness);
        ledPixels.show(); 
        delay(delayBlinks);
      }
}

//***UPDATE RGB LED COLOR FUNCTION***//

void updateLedColor(int ledColor, uint8_t ledBrightness) {
    ledPixels.setPixelColor(0, ledPixels.Color(colorProperty[ledColor-1].colorCode.g,colorProperty[ledColor-1].colorCode.r,colorProperty[ledColor-1].colorCode.b));
    ledPixels.setBrightness(ledBrightness);
    ledPixels.show();
}

//***GET RGB LED COLOR FUNCTION***//

uint32_t getLedColor(int ledModeNumber) {

  int colorNumber= modeProperty[ledModeNumber-1].modeColorNumber-1;
  
  return (ledPixels.Color(colorProperty[colorNumber].colorCode.g,colorProperty[colorNumber].colorCode.r,colorProperty[colorNumber].colorCode.b));
}

//***GET RGB LED BRIGHTNESS FUNCTION***//

uint8_t getLedBrightness() {
  return (ledPixels.getBrightness());
}

//***SET RGB LED COLOR FUNCTION***//

void setLedColor (uint32_t ledColor, uint8_t ledBrightness){
  ledPixels.setPixelColor(0, ledColor);
  ledPixels.setBrightness(ledBrightness);
  ledPixels.show(); 

}

//***SET RGB LED BRIGHTNESS FUNCTION***//
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

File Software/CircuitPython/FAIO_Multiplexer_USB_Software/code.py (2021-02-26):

#***************************************************************************
#* File Name: FAIO_Multiplexer_USB_Software/code.py
#* Title: FAIO Multiplexer USB CircuitPython Code
#* Developed by: Milador
#* Version Number: 1.0 (25/2/2021)
#* Github Link: https://github.com/milador/FAIO_Multiplexer/tree/master/Software/CircuitPython/FAIO_Multiplexer_USB_Software
#***************************************************************************/

#Import modules
import time
import board
from digitalio import DigitalInOut, Direction, Pull
import usb_hid
import neopixel
led = neopixel.NeoPixel(board.NEOPIXEL, 1)

#Import modules from the Adafruit hid library
from adafruit_hid.keyboard import Keyboard
from adafruit_hid.keycode import Keycode
from adafruit_hid.mouse import Mouse

#Customize values
led.brightness = 0.3
switch_time_delay = 0.125
switch_debug_mode = False    #To serial print = True , To not serial print = False
switch_operation_mode = 1    #Keyboard = 1, Mouse = 2
switch_mac_mode = False      #To use keys for mac = True , To use keys for other os = False


#Mac mode or other keyboard mode actions
if switch_mac_mode:
    switch_a_keyboard_action = Keycode.F1
    switch_b_keyboard_action = Keycode.F2
    switch_c_keyboard_action = Keycode.F3
    switch_d_keyboard_action = Keycode.F4
else:
    switch_a_keyboard_action = Keycode.A
    switch_b_keyboard_action = Keycode.B
    switch_c_keyboard_action = Keycode.C
    switch_d_keyboard_action = Keycode.D

#Mouse actions
switch_a_mouse_action = Mouse.LEFT_BUTTON
switch_b_mouse_action = Mouse.RIGHT_BUTTON
switch_c_mouse_action = Mouse.MIDDLE_BUTTON
switch_d_mouse_action = "DRAG"

time.sleep(1)

# Define buttons
button_a = DigitalInOut(board.D0)
button_a.direction = Direction.INPUT
button_a.pull = Pull.UP

button_b = DigitalInOut(board.D2)
button_b.direction = Direction.INPUT
button_b.pull = Pull.UP

button_c = DigitalInOut(board.D11)
button_c.direction = Direction.INPUT
button_c.pull = Pull.UP

button_d = DigitalInOut(board.D6)
button_d.direction = Direction.INPUT
button_d.pull = Pull.UP

#Creates a keyboard instance
keyboard = Keyboard(usb_hid.devices)

# Define colors
led_color_teal = (0, 128, 128)
led_color_blue = (0, 0, 255)
led_color_yellow = (150, 255, 0)
led_color_green = (0, 255, 0)
led_color_red = (255, 0, 0)

#Initial led color
led[0] = led_color_teal

#Setup mouse
mouse = Mouse(usb_hid.devices)
mouse_state = 0

time.sleep(.5)
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

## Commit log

2019-02-19 Added the PCB Files.
    [FAIO2.brd, FAIO2.sch]
2019-02-19 Moved PCB files
    [FAIO2.brd, FAIO2.sch]
2019-02-19 Moved the PCB files
    [FAIO2.brd, FAIO2.sch]
2019-02-19 Added BOM file
    [FAIO-2_BOM.xlsx]
2019-02-24 CSV version of BOM
    [FAIO-2_BOM.csv]
2019-02-25 Changed naming convention
    [FAIO2_Switch.brd, FAIO2_Switch.sch]
2019-02-26 Added Sip and puff module PCB files
    [FAIO2_Sip-n-Puff.brd, FAIO2_Sip-n-Puff.sch]
2019-02-26 Updated BOM Files
    [FAIO-2_Switch_BOM.csv, FAIO-2_Switch_BOM.xlsx]
2019-04-20 Changed FAIO project github page to two separate projects
    [FAIO-2_Switch_BOM.xlsx, FAIO-Multiplexer_BOM.csv, FAIO-Multiplexer_BOM.xlsx, FAIO2_Sip-n-Puff.brd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]
2019-04-20 Changed BOM file name
    [FAIO_Multiplexer_BOM.csv, FAIO_Multiplexer_BOM.xlsx]
2019-04-21 Corrected resistor value
    [FAIO_Multiplexer_BOM.csv, FAIO_Multiplexer_BOM.xlsx]
2019-09-30 Added the enclosure STL files and the instructions manual
    [FAIO_Multiplexer_Body_Battery_Holder.stl, FAIO_Multiplexer_Body_Bottom.stl, FAIO_Multiplexer_Body_Top.stl]
2020-04-13 New stl files
    [FAIO-Joystick-Bottom-Box.stl, FAIO-Joystick-Handle.stl, FAIO-Joystick-Top-Box.stl]
2020-07-24 Updated code: Fixed typo in description, Removed Wireless BOM file
    [FAIO_Multiplexer_BOM.csv, FAIO_Multiplexer_BOM.xlsx]
2020-11-29 Updated STL files
    [FAIO-Joystick-Bottom-Box.stl, FAIO-Joystick-Handle.stl, FAIO-Joystick-Top-Box.stl, FAIO_Multiplexer_Body_Battery_Holder.step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]
2020-11-29 Removed untested files
    [FAIO-Joystick-Bottom-Box.stl, FAIO-Joystick-Handle.stl, FAIO-Joystick-Top-Box.stl]
2020-12-20 Updated BOM and added M2.5 screws
    [FAIO_Multiplexer_BOM.csv, FAIO_Multiplexer_BOM.xlsx]
2021-01-11 Updated BOM file for the new enclosure
    [FAIO_Multiplexer_BOM.csv, FAIO_Multiplexer_BOM.xlsx]
2021-01-11 Update Manuals for the new enclosure
2021-01-11 Updated enclosure files : New snap fit enclosure
    [FAIO_Multiplexer_Body_Battery_Holder.step, FAIO_Multiplexer_Body_Battery_Holder.stl, FAIO_Multiplexer_Body_Bottom.step, FAIO_Multiplexer_Body_Bottom.stl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]
2021-01-12 Updated enclosure file links
2021-01-12 Updated enclosure STL files (2.7mm holder holes)
    [FAIO_Multiplexer_Body_Battery_Holder.step, FAIO_Multiplexer_Body_Battery_Holder.stl, FAIO_Multiplexer_Body_Bottom.step, FAIO_Multiplexer_Body_Bottom.stl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]
2021-01-17 Updated Enclosure : Snap wall height was increased by 0.8mm.
    [FAIO_Multiplexer_Body_Battery_Holder.step, FAIO_Multiplexer_Body_Battery_Holder.stl, FAIO_Multiplexer_Body_Bottom.step, FAIO_Multiplexer_Body_Bottom.stl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]
2021-01-18 Updated Manuals : Updated enclosure images
2021-01-18 Added PCB gerber files
    [FAIO_Multiplexer.brd]
2021-01-31 Updated Assembly manual 1.11
2021-03-13 Updated PCB Files: 2.0 text changed to Multiplexer
    [FAIO_Multiplexer.brd, FAIO_Multiplexer.sch]

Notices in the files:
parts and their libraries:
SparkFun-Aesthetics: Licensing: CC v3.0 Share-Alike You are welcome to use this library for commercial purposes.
